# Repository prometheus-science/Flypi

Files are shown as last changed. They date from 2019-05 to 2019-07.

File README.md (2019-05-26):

#### Flypi - An open source, modular, affordable tool for imaging experiments.

Hi! Thanks for dropping by. This project started during one of the summer courses organized by [Trend in Africa](www.trendinafrica.org). It developed to the current state due to the efforts of many people along the way. In special Tom Baden, Lucia Prieto, and Edwin Cruz. A paper describing the system was published in [Plos Biology](http://journals.plos.org/plosbiology/article?id=10.1371/journal.pbio.2002702).

 Version 1.0 was released with the paper and can be found [here](https://github.com/amchagas/Flypi/tree/v1.0.0).

The system can be used for optical microscopy, fluorescence, behavioural tracking, optogenetics, calcium imaging and thermogenetics (see examples recorded with the system below).

##### Further development is being done by [Prometheus Science](https://www.prometheus-science.com)

#### Some samples imaged with the device:

Fluorescence ZebraFish GFP expressed in heart tissue|
GCamP_ZebraFish|Zebra Fish Transmission
--|---|--
C.Elegans behaviour|Drosophila Crimson | Drosophila walking about

### We've created a Forum for users to posts questions and suggestions too! Please take a look [here](http://forum.prometheus-science.com/home/categories/flypi-user-forum)

### Custom PCB

You can order the PCBs and buy the parts to assemble them through the [Kitspace page](https://kitspace.org/boards/github.com/prometheus-science/FlyPi).

#### Necessary Libraries:

LED Ring from Adafruit:
https://github.com/adafruit/Adafruit_NeoPixel

LED Matrix from Adafruit:
https://github.com/adafruit/Adafruit-LED-Backpack-Library

gpac library:
sudo apt-get update
sudo apt-get install gpac

## *.h264 conversion to *.avi:
Done via gpac. MP4BOX.

## SD Card image containing Raspian image with all things installed:
https://www.dropbox.com/sh/bibhy2sgadq30dm/AACD2Rdhmad2QdBi9q-pQfd6a?dl=0

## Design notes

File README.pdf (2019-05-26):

Flypi - An open source, modular,

# affordable tool for imaging

experiments.

## Initially developed by Trend in Africa and published in

Plos Biology. (http://journals.plos.org/plosbiology/article?id=10.1371/journal.pbio.2002702)

Version 1.0 was released with the paper and can be found here. (https://github.com/amchagas/Flypi/tree/v1.0.0)

The system can be used for optical microscopy, fluorescence,

### behavioural tracking, optogenetics, calcium imaging and

thermogenetics.

### Further development is being done by Prometheus Science

### Some samples imaged with the device:

![Fluorescence ZebraFish GFP expressed in heart tissue] (example_samples/PLOS_Paper/Zebrafish heartbeat GFP.gif) |

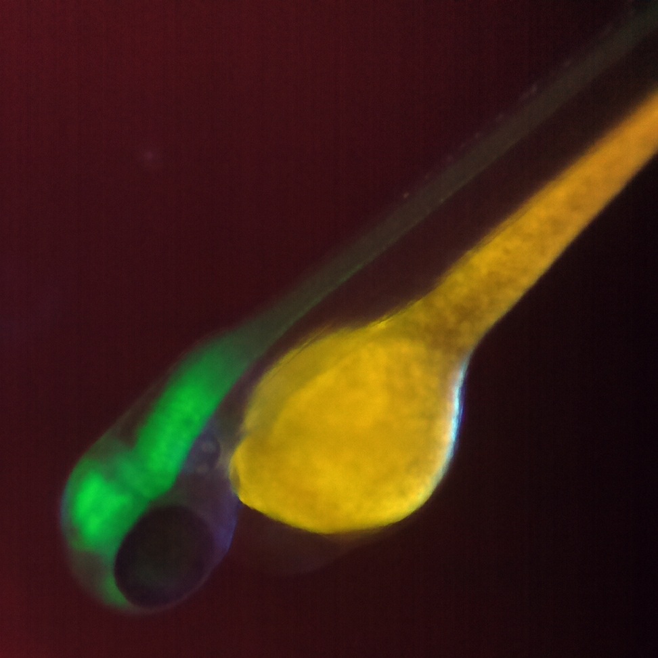
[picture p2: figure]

| test2
4 | 5 | 6
10 | 11 | 12

## We've created a Forum for users to posts questions and

suggestions too! Please take a look here (http://forum.prometheus-science.com/home/categories/flypi-user-forum)

# Custom PCB

You can order the PCBs and buy the parts to assemble them through the Kitspace page. (https://kitspace.org/boards/github.com/prometheus-science/FlyPi)

# Necessary Libraries:

LED Ring from Adafruit:
https://github.com/adafruit/Adafruit_NeoPixel

LED Matrix from Adafruit:
https://github.com/adafruit/Adafruit-LED-Backpack-Library

gpac library:
sudo apt-get update
sudo apt-get install gpac

libav library:
sudo apt-get update
sudo apt-get install libav-tools

update pyserial library:
sudo pip3 install --upgrade serial

# *.h264 conversion to *.avi:

is done via avconv (which is installed with libav-tools).

# SD Card image containing Raspian image with all things installed:

https://www.dropbox.com/sh/bibhy2sgadq30dm/AACD2Rdhmad2QdBi9q-pQfd6a?dl=0

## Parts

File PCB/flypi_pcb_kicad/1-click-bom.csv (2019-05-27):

References | Qty | Description | Manufacturer | MPN | Manufacturer_1 | MPN_2 | Manufacturer_3 | MPN_4 | Manufacturer_5 | MPN_6 | Manufacturer_7 | MPN_8 | Digikey | Mouser | RS | Newark | Farnell
U5; | 2 | Headers 15 pin 1 row | Samtec inc | SSA-115-S-T | Samtec Inc | SSW-115-01-T-S | Amphenol | 75915-315LF |  |  |  |  | SAM1122-15-ND | 200-SSW11501TS | 859-9390 | 11P7739 | 2779587
U4; | 1 | L298N Multiwatt 15 Vertical | STMicroelectronics | L298N |  |  |  |  |  |  |  |  | 497-1395-5-ND | 511L298 | 636384 | 32M1527 | 403295
U1; U2 | 2 | LM2596 5v | ITO-220 | Texas Instruments | Texas Instruments | LM2596T-5.0/NOPB |  |  |  |  |  |  | LM2596T-5.0/NOPB-ND | 926LM2596T5.0/NOPB | 5333743 | 97K3256 | 1150103
R7; R8; R9 | 3 | Resistor 220 ohm 250mW through-hole | Yageo | MFR-25FBF52-220R | TE Connectivity | CBT25J220R | TE Connectivity | CFR16J220R | Ohmite | OD221JE | Stackpole Electronics | CF14JT220R | CF14JT220RCT-ND | 279CBT25J220R | 8066376 | 21R0186 | 1265068
R2; R3; R4; R5 | 4 | Resistor 270 ohm 250mW through-hole | Stackpole Electronics | CF14JT270R | Yageo | MFR-25FBF52-220R | TE Connectivity | CFR16J270R | Ohmite | OD271JE | Kamaya | RC1/4271JB | CF14JT270RCT-ND | 791-RC1/4-271JB | 148360 | 95W5736 | 2329504
R1; | 1 | Resistor 20W TO-220 | Bourns | PWR220T-20-R500F |  |  |  |  |  |  |  |  | PWR220T-20-R500F-ND | 652PWR220T20R500F | 7962508 | 55R1098 | 2328267
Q1; Q2; Q3; Q4; Q1 | 4 | 1A NPN | ON Semiconductor/fairchild | PN2222ATF |  |  |  |  |  |  |  |  | PN2222ATFCT-ND | 512-PN2222ATF | 806-1296 | 31Y3451 | 2453811
P9; | 1 | Header 4 pin 1 row | Sullins | PPTC041LFBN-RC | Amp TE connectivity | 147721-3 |  |  |  |  |  |  | S7002-ND | 571-215297-4 | 4958543 | 98K6514 | 3419060
P10; | 1 | CONN HEADER XH TOP 4POS 2.5MM | JST | B4B-XH-A (LF)(SN) |  |  |  |  |  |  |  |  | 455-2249-ND |  | 820-1551 |  | 1516278
P4; P7; P8; | 3 | CONN HEADER XH TOP 3POS 2.5MM | JST | B3B-XH-A (LF)(SN) |  |  |  |  |  |  |  |  | 455-2248-ND |  | 8201557 | 73M9431 | 1516277
P1; P3; P5; P6; | 4 | CONN HEADER XH TOP 2POS 2.5MM | JST | B2B-XH-A (LF)(SN) |  |  |  |  |  |  |  |  | 455-2247-ND |  | 8201554P | 73M9415 | 1516276
L1; L2; | 2 | INDUCTOR 33µH Neosid MA-Bs75 | Bourns | RLB0914-330KL |  |  |  |  |  |  |  |  | RLB0914-330KL-ND | 652RLB0914330KL | 8118853 | 61J7916 | 2309242
J12; | 1 | USB A Vertical | FCI | 73725-0110BLF | Molex | 48204-0001 |  |  |  |  |  |  | 609-1041-ND | 649737250110BLF | 7710048 | 56R0832 | 2782046
D1; D3; | 2 | Diode Schottky 5A DO-201AD | Vishay | 1N5822-E3/73 | Zetex | SB5100-T |  |  |  |  |  |  | 1N5822-E3/73GICT-ND | 6251N5822E3/73 | 751-4843 | 17T8202 | 1336553
CON1; | 1 | 2.1mm socket | Cliff | FC68148 DC10A | Lumberg | NEB 21 R | Cliff | FC68148 | Gravitech | CON-SOCJ-2155 | Parallax | 452-00007 | 452-00007-ND | 992CONSOCJ2155 | 5051609 | 08WX2563 | 224959
C6; C5; | 2 | CAP ALUM 220UF 20% 25V RADIAL | Panasonic | EEU-FM1E221 | Panasonic | ECA-1CM221B | Panasonic | ECE-A0GKS221 | Panasonic | EEU-EB1A221S |  |  | P12383-ND | 667ECA1CM221B | 7472036 | 70K9673 | 9451099
C2; C1; | 2 | 680µF Capacitor | Rubycon | 16ZL680MEFC10X16 | Panasonic | EEU-FC1A681 | Panasonic | EEU-FP1E681 |  |  |  |  | 1189-3978-ND | 667-EEU-FP1E681 | 7037258 | 31M6417 | 1144691
C10; C7; C8; | 3 | 100nF Capacitor Disc | Multicomp | MCFYU6104Z6 | KEMET | C052C104K5R5CA | KEMET | C052K104K5X5CA | KEMET | C052T104K5X5CS | KEMET | C321C104K5R5HA | BC1160CT-ND | 80C321C104K5R5HA | 852-3277 | 73M2154 | 2395773
1k1; | 1 | Resistor 1k 250mW through-hole | Multicomp | MF12 1K | Yageo | MFR-25FBF52-1K | RS Pro | 7077666 |  |  |  |  | 1.00KXBK-ND | 603MFR25FBF521K | 7077666 | 38K5400 | 9342400
MCU; | 1 | Arduino Mini | Arduino | A000087 | Arduino | A000005 |  |  |  |  |  |  | 1050-1001-ND | 992-ARD-NANO30 | 696-1667 | 13T9275 | 1848691
2 pin housing; | 4 | plastic housing for crimped cables 2 pins XH | JST | XHP-2 |  |  |  |  |  |  |  |  | 455-2266-ND |  | 1667314 |  | 1516264
3 pin housing; | 3 | plastic housing for crimped cables 3 pins XH | JST | XHP-3 |  |  |  |  |  |  |  |  | 455-2219-ND | 941-XHP35A0D0BD440E | 8201614 |  | 1516265
4 pin housing; | 1 | plastic housing for crimped cables 4 pins XH | JST | XHP-4 |  |  |  |  |  |  |  |  | 455-2267-ND |  | 1667316 | 74M5179 | 1516266
Crimped cable; | 21 | cables crimped with XH connectors | JST | ASXHSXH22K305 | JST | 01SXHSXH-26L 300 |  |  |  |  |  |  | 455-3241-ND |  | 820-1541
fan; | 1 | 36X36mm 5V cooling fan | Multicomp | MC36256 | NMB Technologies | 03510SS-05N-AT-00 | Sunon | MF35100V2-1000U-A99 |  |  |  |  | P19864-ND | 369-MF35100V21UA99 | 798-0754 | 23T0585 | 1924855
hdmi cable; | 1 | HDMI Cable (Raspberry to monitor) | Raspberry Pi | CPRP010-W | Tripp lite | P569-001 | Qualtek | 1721001-03 | RS pro | 801-1196 |  |  | TL1665-ND | 562-1721001-03 | 801-1196 |  | 2545201
Raspberry Pi; | 1 | Rasbperry Pi 3 | Raspberry Pi | RASPBERRYPI3-MODB-1GB | Seeed studio | 114990584 |  |  |  |  |  |  | 1690-1000-ND | 713-114990584 | 8326274 |  | 2525225
USB cable micro; | 1 | USB A to micro B | Tripp Lite | UR050-06N | rolline | 11.02.8310 | RS Pro | 121-6579 |  |  |  |  | TL1234-ND | 545-UR050-06N | 121-6579 | 68X4607 | 2444222
USB cable mini; | 1 | USB A to mini B | Tripp Lite | UR030-06N | RS-pro | 121-6572 |  |  |  |  |  |  | TL1233-ND | 545-UR030-06N | 121-6572 | 68X4592 | 2751173
LED Ring; | 1 | LED ring 12 leds | Adafruit | 1643 |  |  |  |  |  |  |  |  | 1528-1102-ND | 485-1643
RGB Led; | 1 | RGB LED 4 pins | Knight bright | WP154A4SUREQBFZGC | knight bright | L-154A4SUREQBFZGEW |  |  |  |  |  |  | 754-1615-ND | 604-WP154A4SUREQBFZG | 8614294 | 66W1972 | 2290375
SD card; | 1 | Class 10 16GB sd microsd | Apacer Memory America | AP16GMCSH10U1-B | Verbatim | 44082 |  |  |  |  |  |  | 1582-1004-ND | 908-AP16GMCSH10U1-B | 877-5557
Peltier module; | 1 | 40X40X3.8mm peltier module | CUI Inc | CP85438 | P&NTechnology | TEC1-127050 | Multicomp | MCPE1-12707AC-S | Adaptive | ET-127-14-11-RS |  |  | 102-1682-ND | 490-CP85438 | 490-1373 | 08P1446 | 1639722
heatsink; | 2 | 36X36X12 aluminum heatsink | CTS Thermal Management Products | BDN14-3CB/A01 | Fischer eletronik | ICK S 36 X 36 X 10 |  |  |  |  |  |  | 294-1101-ND | 774-BDN143CBA01 | 6744810 | 74M2393 | 1211714
UV led; | 1 | EMITTER UV 390NM 1A | LED Engin inc | LZ1-10UB00-00U4 |  |  |  |  |  |  |  |  | 1537-1137-ND |  | 9053905P
temperature sensor; | 1 | analog output | Analog devices | AD22100KTZ |  |  |  |  |  |  |  |  | AD22100KTZ-ND | 584-AD22100KTZ | 5230076 |  | 9605320
power supply; | 1 | 12V 5A output | Mean well | GSM60A12-P1J | CUI | SDI65-12-U2-P5 |  |  |  |  |  |  | 1866-2016-ND | 490-SDI65-12-U2-P5 | 7911058 | 44AC5087 | 2815822
picamera; | 1 | 5MP 12mm focal distance lens (m12 thread) | waveshare | 8193 | https://www.waveshare.com/product/mini-pc/raspberry-pi/cameras/rpi-camera-b.htm

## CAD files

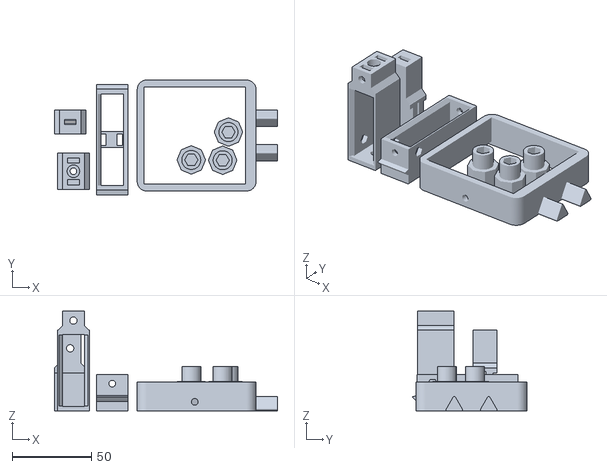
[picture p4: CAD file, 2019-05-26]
3D_print_files/v2.0/STLs/plates/Manipulator_complete.stl
140.7 x 72.5 x 63.0

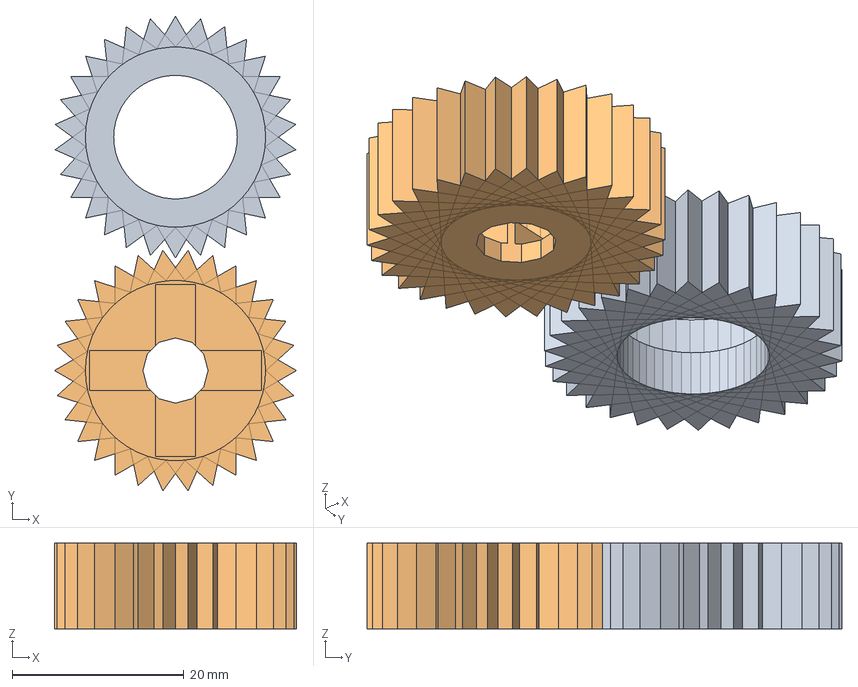
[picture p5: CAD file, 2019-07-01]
3D_print_files/v2.0/STEPs/Camera_servo_gears.step
28.2 x 55.3 x 10.0 mm

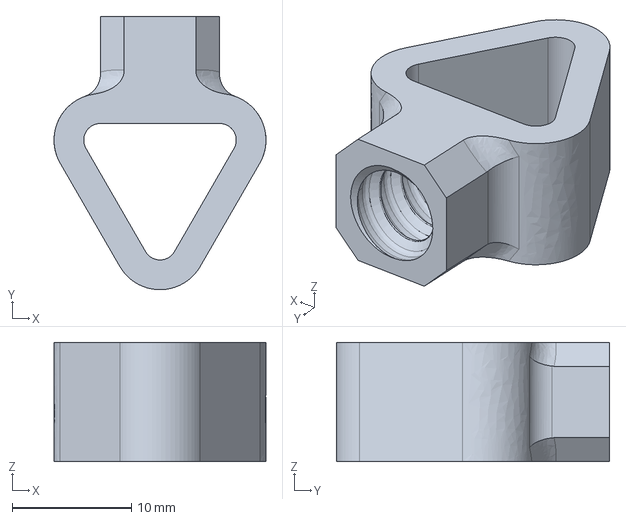
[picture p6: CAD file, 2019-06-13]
3D_print_files/v2.0/STEPs/parts_for_development/Neck_triangle.step
17.8 x 23.0 x 10.0 mm

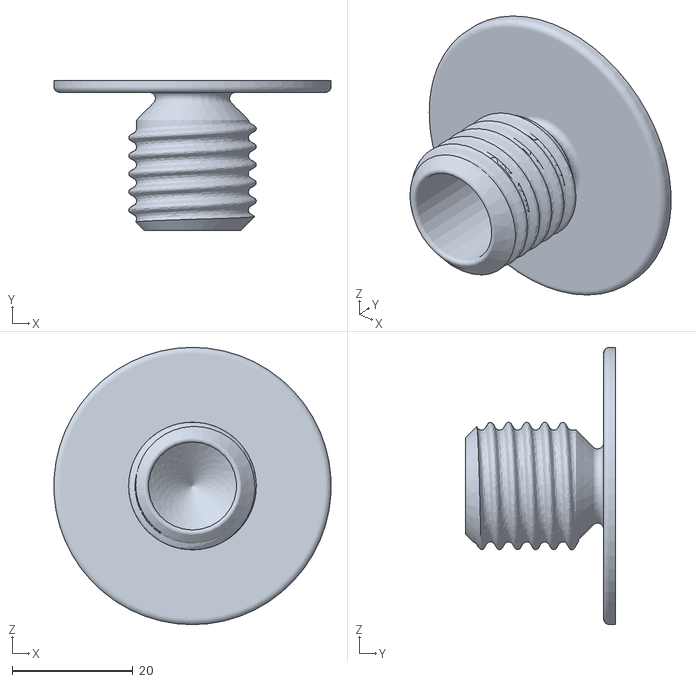
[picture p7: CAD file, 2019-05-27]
3D_print_files/v2.0/STLs/LED_ring_light_diffuser_use_transp_filament.stl
45.9 x 24.9 x 46.0

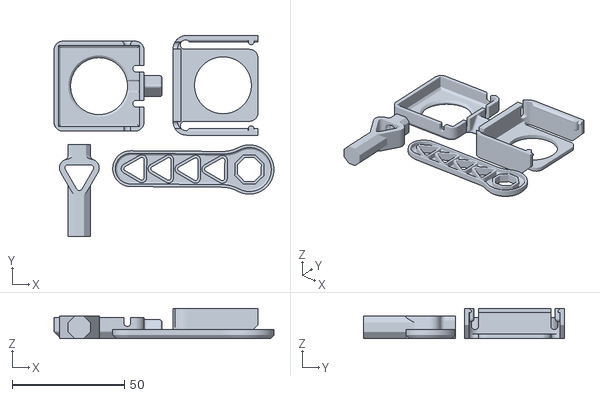
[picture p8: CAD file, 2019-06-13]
3D_print_files/v2.0/STLs/plates/HP_led.stl
98.2 x 89.8 x 13.4

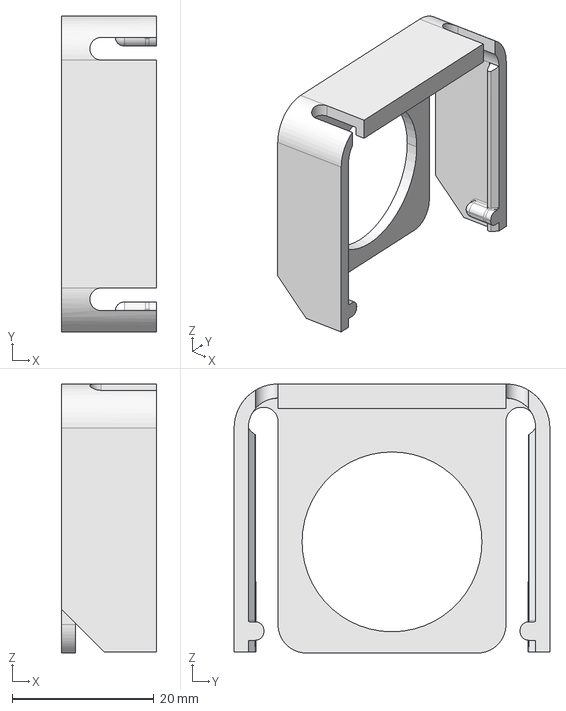
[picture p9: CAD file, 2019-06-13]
3D_print_files/v2.0/STEPs/HP_led_filter_holder.step
13.4 x 44.6 x 38.0 mm

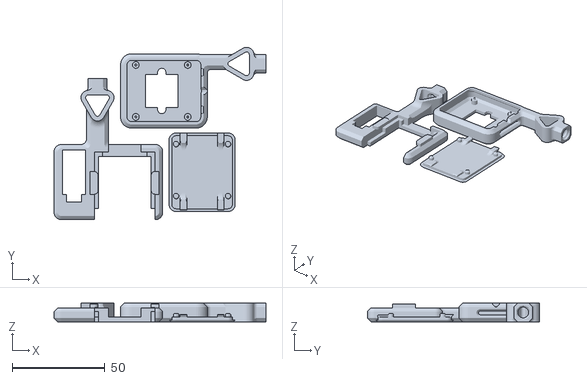
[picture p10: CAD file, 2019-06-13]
3D_print_files/v2.0/STLs/plates/Camera.stl
114.1 x 92.8 x 10.00

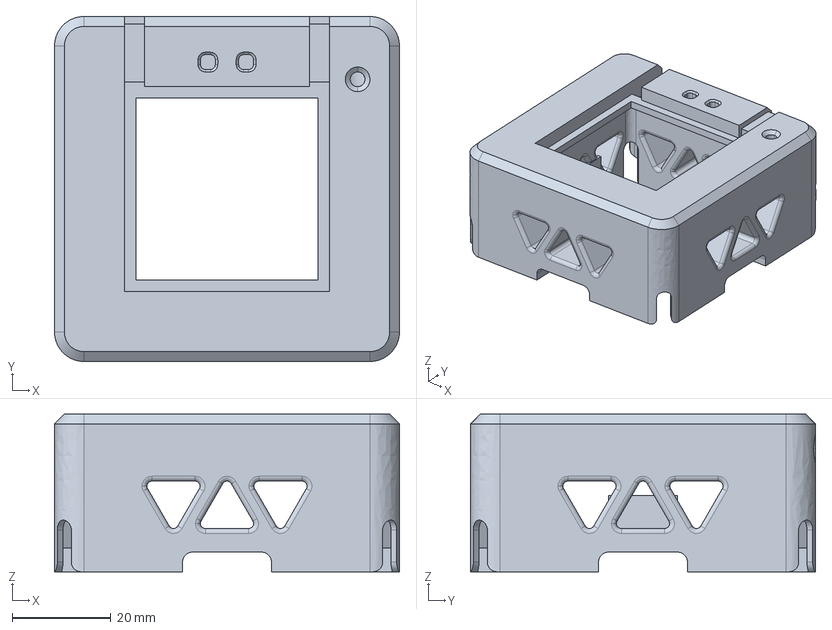
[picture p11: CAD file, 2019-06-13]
3D_print_files/v2.0/STEPs/Base.step
70.0 x 70.0 x 32.0 mm

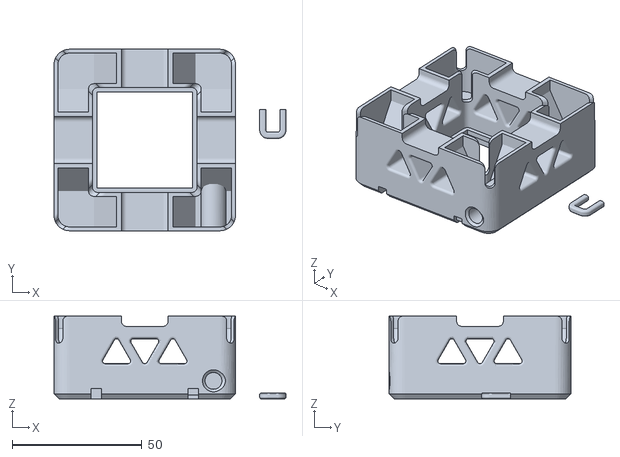
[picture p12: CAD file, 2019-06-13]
3D_print_files/v2.0/STLs/plates/Base.stl
89.5 x 70.0 x 32.0

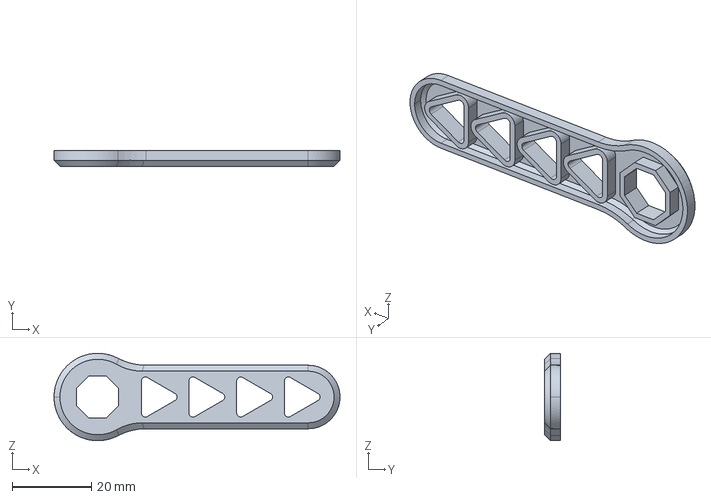
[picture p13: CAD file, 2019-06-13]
3D_print_files/v2.0/STEPs/HP_led_holder_arm.step
72.0 x 4.00 x 22.0 mm

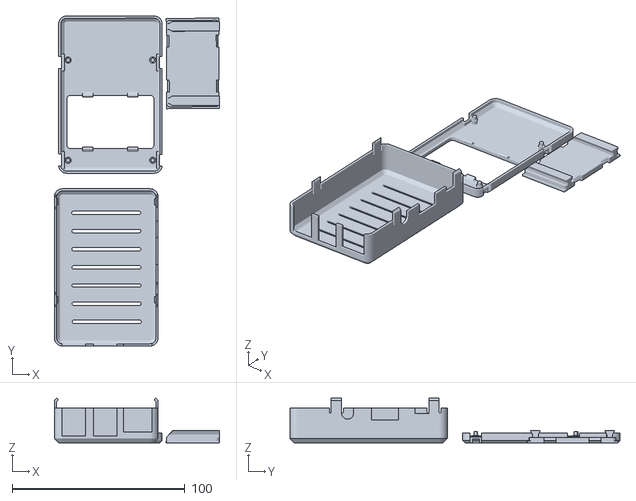
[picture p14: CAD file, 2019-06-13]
3D_print_files/v2.0/STLs/plates/Raspberry_case.stl
95.6 x 190.9 x 25.9

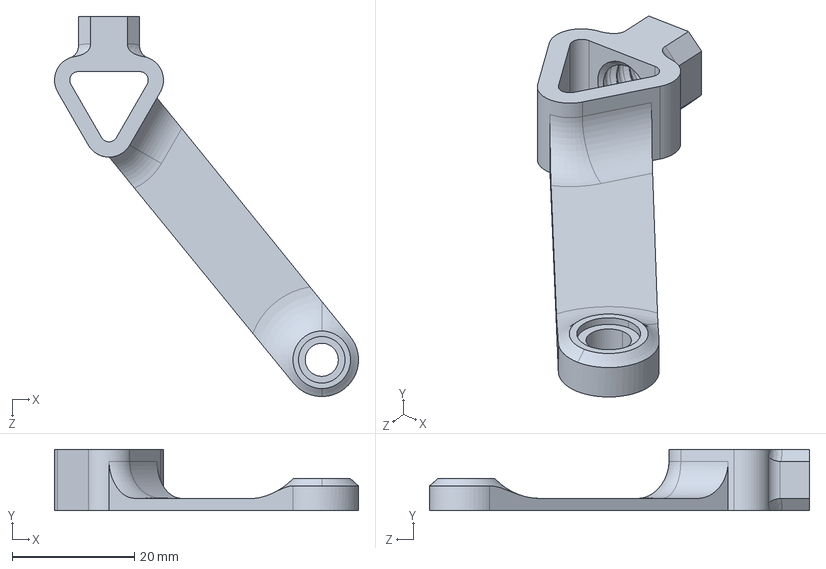
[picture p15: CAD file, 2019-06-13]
3D_print_files/v2.0/STEPs/Fluorescence_filter_arm.step
49.6 x 10.0 x 62.1 mm

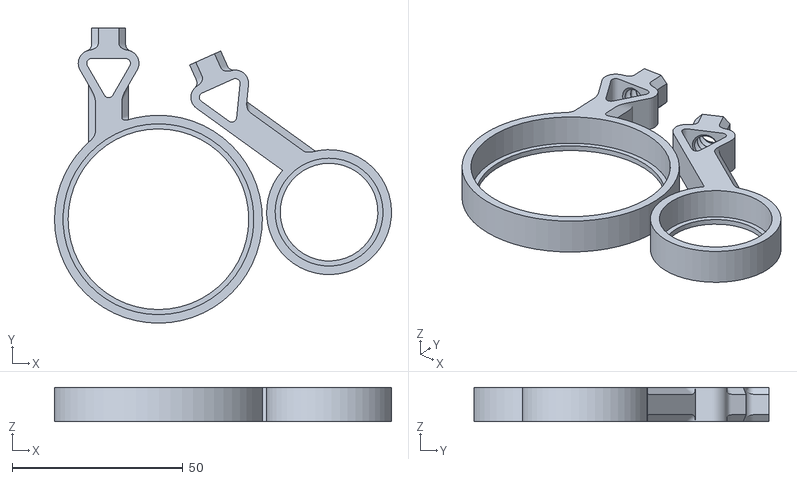
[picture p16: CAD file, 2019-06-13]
3D_print_files/v2.0/STLs/plates/Petri_dishes.stl
98.7 x 86.5 x 10.0

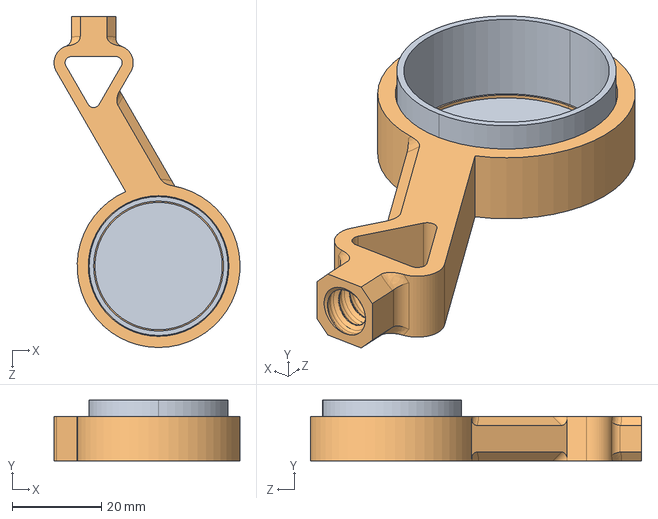
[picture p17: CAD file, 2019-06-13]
3D_print_files/v2.0/STEPs/PetriDish_36mm.step
41.8 x 13.7 x 74.4 mm

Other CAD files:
3D_print_files/v2.0/STLs/plates/Fluorescence.stl
3D_print_files/v2.0/STEPs/Raspberry_case_rails.step
3D_print_files/v2.0/STLs/plates/LED_ring_holder.stl
3D_print_files/v2.0/STEPs/Fluorescence_filter_arm_cross.step
3D_print_files/v1.0/Fly-Pi manipulator_v5.scad
3D_print_files/v2.0/STEPs/Base_clip.step
3D_print_files/v2.0/STEPs/Camera_Cap.step
3D_print_files/v2.0/STEPs/Camera_Housing.step
3D_print_files/v2.0/STEPs/Camera_servo_holder.step
3D_print_files/v2.0/STEPs/Electronics_to_sample.step
3D_print_files/v2.0/STEPs/Fluorescence_light_guide.step
3D_print_files/v2.0/STEPs/HP_led_heatsink_holder.step
3D_print_files/v2.0/STEPs/HP_led_holder_angular_arm.step
3D_print_files/v2.0/STEPs/LED_ring_holder.step
3D_print_files/v2.0/STEPs/LED_ring_light_diffuser.step
3D_print_files/v2.0/STEPs/Manipulator_Xaxis.step
3D_print_files/v2.0/STEPs/Manipulator_Zaxis.step
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

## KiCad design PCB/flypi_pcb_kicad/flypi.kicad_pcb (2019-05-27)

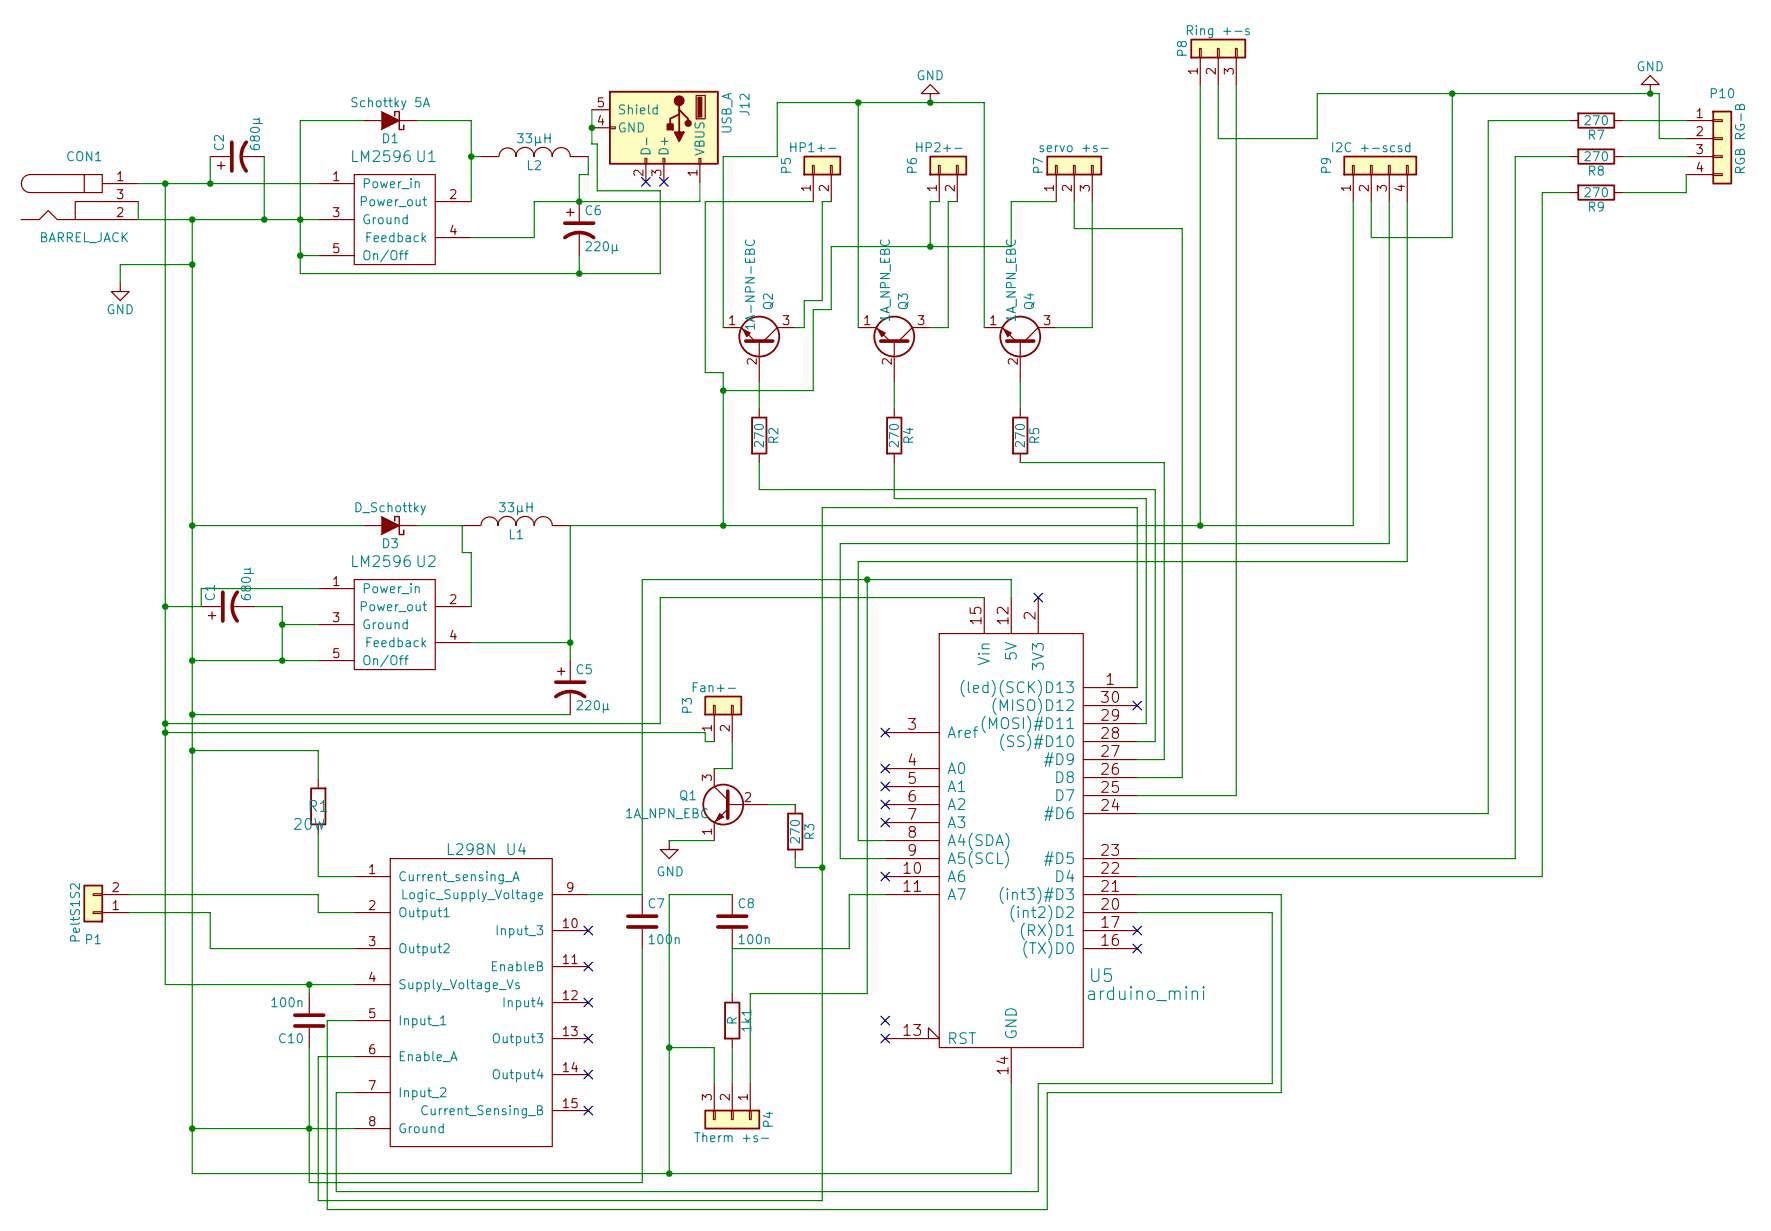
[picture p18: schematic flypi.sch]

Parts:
1k1: R; R_Axial_DIN0411_L9.9mm_D3.6mm_P12.70mm_Horizontal
C1, C2: 680µ; C_Radial_D10_L21_P5
C5, C6: 220µ; C_Radial_D8_L13_P3.8
C7, C8, C10: 100n; C_Disc_D3_P2.5
CON1: BARREL_JACK
D1: Schottky 5A; Diode_DO-201AD_Horizontal_RM15
D3: D_Schottky; Diode_DO-201AD_Horizontal_RM15
J12: USB_A; USB_A_Vertical
L1, L2: 33µH; Neosid_Inductor_MA-Bs75
P1: PeltS1S2; JST_EH_S02B-EH_02x2.50mm_Angled
P3: Fan+-; JST_EH_S02B-EH_02x2.50mm_Angled
P4: Therm +s-; JST_EH_S03B-EH_03x2.50mm_Angled
P5: HP1+-; JST_EH_S02B-EH_02x2.50mm_Angled
P6: HP2+-; JST_EH_S02B-EH_02x2.50mm_Angled
P7: servo +s-; JST_EH_S03B-EH_03x2.50mm_Angled
P8: Ring +-s; JST_EH_S03B-EH_03x2.50mm_Angled
P9: I2C +-scsd; Socket_Strip_Straight_1x04_Pitch2.54mm
P10: RGB RG-B; JST_EH_S04B-EH_04x2.50mm_Angled
Q1, Q3, Q4: 1A_NPN_EBC; TO-92_Inline_Wide
Q2: 1A-NPN-EBC; TO-92_Inline_Wide
R1: 20W; TO-220-2_Vertical
R2, R3, R4, R5, R7, R8, R9: 270; R_Axial_DIN0411_L9.9mm_D3.6mm_P12.70mm_Horizontal
U1, U2: LM2596
U4: L298N; Multiwatt_15_Vertical
U5: arduino_mini; DIP-30_W15.24mm_LongPads

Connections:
GND: C1.2, C2.2, C5.2, C6.2, C7.2, C8.1, C10.1, CON1.2, CON1.3, D1.2 (A), D3.2 (A), J12.4 (GND), J12.5 (Shield), P4.3, P8.2, P9.2, P10.2, Q1.1 (E), Q2.1 (E), Q3.1 (E), Q4.1 (E), R1.2, U1.3 (Ground), U1.5 (On/Off), U2.3 (Ground), U2.5 (On/Off), U4.8 (Ground), U5.14 (GND), U5.19 (GND)
unnamed: 1k1.1, C8.2, U5.11 (A7)
unnamed: 1k1.2, P4.2
unnamed: C1.1, C2.1, C10.2, CON1.1, P3.1, U1.1 (Power_in), U2.1 (Power_in), U4.4 (Supply_Voltage_Vs), U5.15 (Vin)
unnamed: C5.1, L1.2, P5.1, P6.1, P7.1, P8.1, P9.1, U2.4 (Feedback)
unnamed: C6.1, J12.1 (VBUS), L2.2, U1.4 (Feedback)
unnamed: C7.1, P4.1, U4.9 (Logic_Supply_Voltage), U5.12 (5V)
unnamed: D1.1 (K), L2.1, U1.2 (Power_out)
unnamed: D3.1 (K), L1.1, U2.2 (Power_out)
unnamed: P1.1, U4.3 (Output2)
unnamed: P1.2, U4.2 (Output1)
unnamed: P3.2, Q1.3 (C)
unnamed: P5.2, Q2.3 (C)
unnamed: P6.2, Q3.3 (C)
unnamed: P7.2, U5.26 (D8)
unnamed: P7.3, Q4.3 (C)
unnamed: P8.3, U5.25 (D7)
unnamed: P9.3, U5.9 (A5(SCL))
unnamed: P9.4, U5.8 (A4(SDA))
unnamed: P10.1, R7.1
unnamed: P10.3, R8.1
unnamed: P10.4, R9.1
unnamed: Q1.2 (B), R3.1
unnamed: Q2.2 (B), R2.1
unnamed: Q3.2 (B), R4.1
unnamed: Q4.2 (B), R5.1
unnamed: R1.1, U4.1 (Current_sensing_A)
unnamed: R2.2, U5.28 ((SS)#D10)
unnamed: R3.2, U4.6 (Enable_A), U5.1 ((led)(SCK)D13)
unnamed: R4.2, U5.29 ((MOSI)#D11)
unnamed: R5.2, U5.27 (#D9)
unnamed: R7.2, U5.24 (#D6)
unnamed: R8.2, U5.23 (#D5)
unnamed: R9.2, U5.22 (D4)
unnamed: U4.5 (Input_1), U5.21 ((int3)#D3)
unnamed: U4.7 (Input_2), U5.20 ((int2)D2)

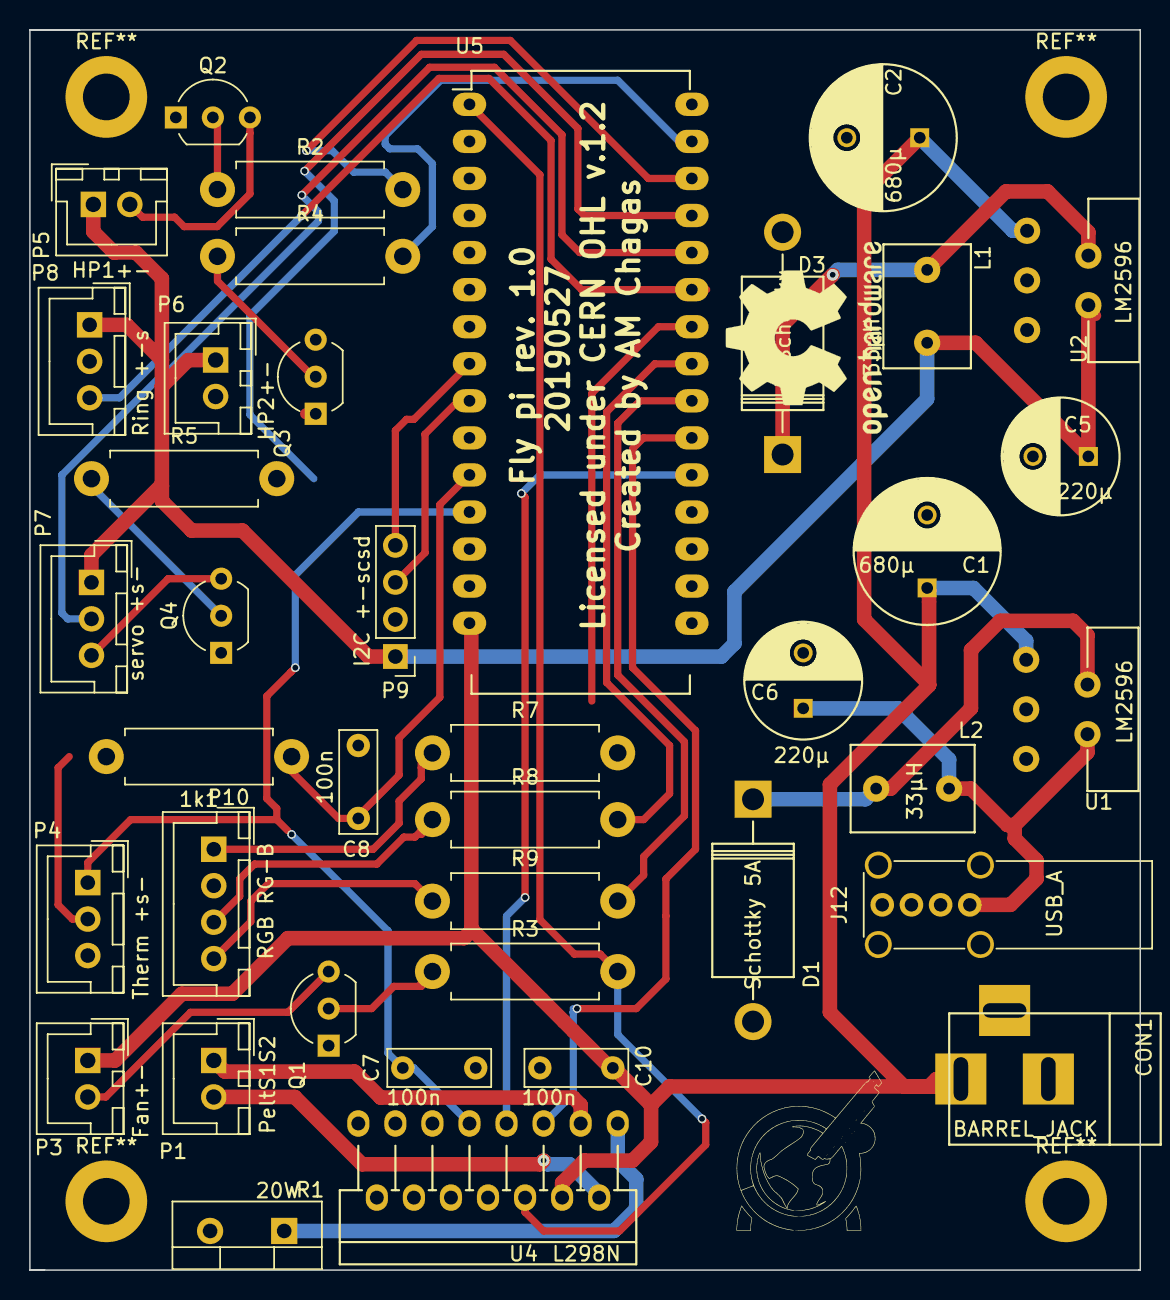
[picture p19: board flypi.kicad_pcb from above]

Board: 2 copper layers, 76.1 x 85.0 mm, 39 parts (0 on the bottom side), 36 nets.

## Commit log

2019-05-27 added light diffuser step and stl
    [LED_Ring_LightDiffuser_print_in_white.stl, Light_funnel.stp, light_diffuser.step, light_diffuser_print_in_white.stl]
2019-05-27 update PCB, change resistor values: 220 for 270, change resistor footprints (shorter footprint), re-wire npn transistors -> now (-) side is being switched on/off, add some logos, change board license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
    [1-click-bom.csv, flypi-2019-05-27-20-30-55.sch, flypi-B.Adhes.gbr, flypi-B.CrtYd.gbr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]
2019-06-13 reorganize 3D print files
    [Base.step, Base.stl, Base.stp, Base_clip.step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]
2019-07-01 added servo gears
    [Camera_servo_gears.step, Camera_servo_gears.stl]
2019-07-04 update base
    [Base.STL, Base.stl]

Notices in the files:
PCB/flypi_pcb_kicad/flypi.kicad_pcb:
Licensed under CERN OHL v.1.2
